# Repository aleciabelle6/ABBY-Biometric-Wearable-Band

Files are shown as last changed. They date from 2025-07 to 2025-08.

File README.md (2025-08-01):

# Anxiety Buddy Band for Youth (ABBY) - Biometric Wearable Band  
_Alecia Barbieri — Princeton University ECE Funded Summer Internship, 2023_

## Project Overview

This repository contains the KiCad design files for a custom Electrodermal Activity (EDA) and heart rate/blood oxygen sensor signal conditioning circuit. It integrates analog signal conditioning stages to filter, amplify, and prepare the weak physiological signals from wearable electrodes and sensors for digitization. This project involved extending and enhancing the Open-Smartwatch-Light open-source platform (https://open-smartwatch.github.io/) by advancing its electronic hardware and serves as my first exposure to KiCAD. 

The circuit is designed to amplify and clean signals from EDA electrodes, with additional capability for heart rate and blood oxygen sensing and position tracking. The design focuses on maximizing signal fidelity through multi-stage amplification and filtering, using a low-power LM324D operational amplifier.

---

## Circuit Extension Design Summary

Taking on this project with no prior experience in PCB design was a very daunting but nonetheless rewarding endeavor. As such, I gained so much knowledge from starting with an open-source PCB layout and extending the functionality of it. Below, I describe the various additions that I made to the design.

### Heart rate and Pulse Sensing

The BH1792GLC-E2 is an optical sensor that measures heart rate and pulse by detecting changes in blood volume using reflected green light. It emits green light through integrated LEDs and captures the reflected signal from skin tissue using a photodiode. This reflected light varies with blood flow, allowing the sensor to extract photoplethysmography (PPG) pulse wave information that is digitized internally and outputt via I2C to the ESP32 microcontroller. The sensor operates with precise timing control and built-in ambient light cancellation for the purpose of enhancing signal quality and reducing noise.

### EDA Sensor Signal Processing

EDA (Electrodermal Activity) electrodes measure changes in skin conductance caused by sweat gland activity, which reflects stress levels. I designed an analog signal conditioning chain that consists of three distinct stages, each implemented using one of the four internal amplifiers in the LM324D quad op-amp IC, for the purpose of having access to noise-free, clear, and useful data that can inform the microcontroller on parts of the physiological makeup that even the user isn't aren't aware of. The raw EDA signal interfaces with the board through an SJ-3524 connector. From there it gets processed through a 3-stage amplifier. The first stage is a differential amplifier stage, which takes in the raw EDA electrode signals, biased with a 1.65 V reference to accommodate single-supply operation and amplifies the differential signal from the electrodes while rejecting common-mode noise and interference. The second stage is an active low-pass filter stage which attenuates high-frequency noise and artifacts, preserving the low-frequency physiological signals typical in EDA and heart rate sensing. The third and final stage is the gain stage, which provides a gain of 11 to bring the signal into an optimal range for analog-to-digital conversion. This conditioned final signal then gets sent to an ADC input that then interfaces with the I2C protocols of the ESP32 at address 0x48.  

### Miscellaneous Changes
I changed the circular Open-Smartwatch-Light into a rectangular board to have enough room to accommodate the new devices. With this, I rerouted the entire board, prioritizing sectioning off analog, digital, and power lines as much as possible with the limited board space and also prioritized having sufficient trace width for the current passing through each branch of the circuit. 

---

## Circuit Component Overview

This section highlights the different components' functions in the circuit as visually depicted in the image below.

<p align="center">
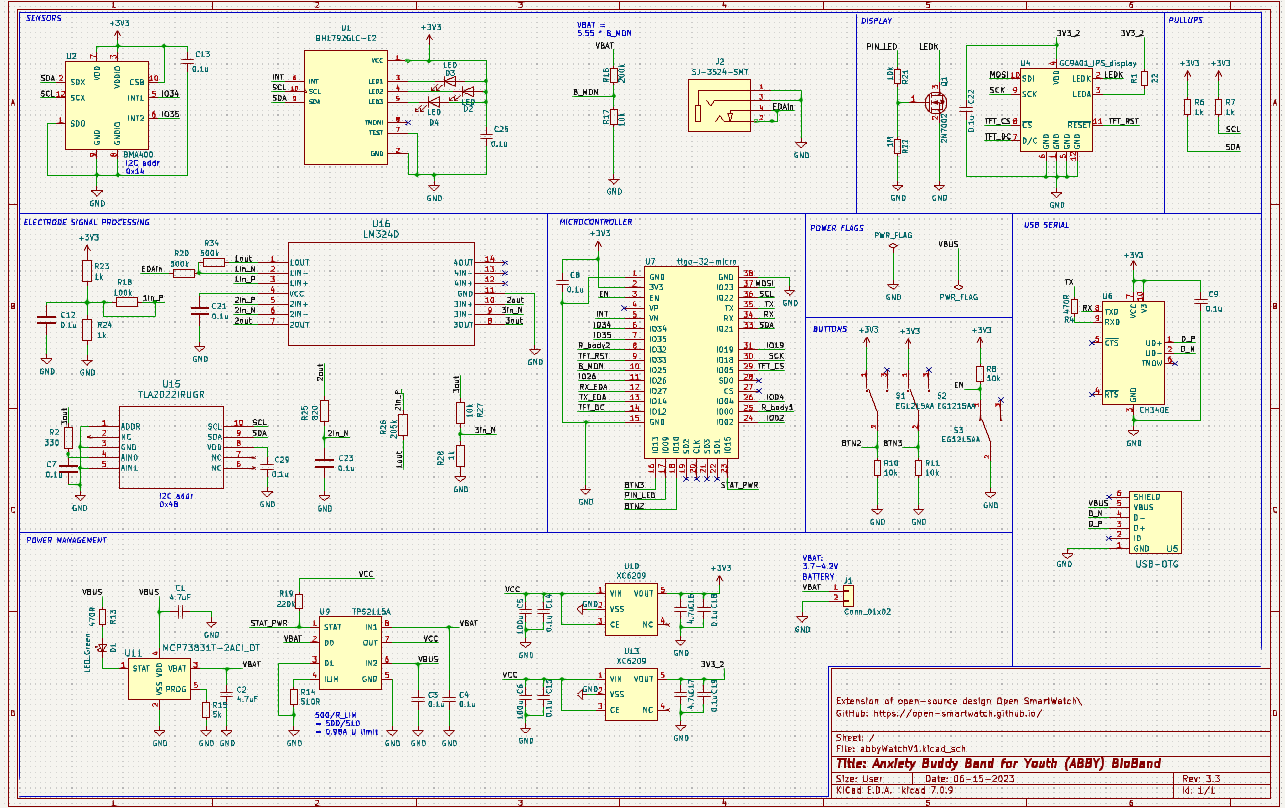
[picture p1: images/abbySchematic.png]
Circuit Schematic
  
</p>

The TTGO T-Micro32 V2.0 (ESP32-based Microcontroller) was used due to its very compact size, coming in at 45% smaller than standard ESP32. It has full GPIO support, Wi-Fi and Bluetooth features, and advanced power-saving features including clock gating, deep sleep, and dynamic power delegation. This microcontroller controls all of the devices, primarily using I2C to communicate with the different sensors as well as the ADC converter.

As far as sensing, the BH1792GLC-E2 ECG/PPG Heart Rate and Oximeter Sensor is an IR-based pulse wave sensor for heart rate and SpO2 monitoring. Communicates via I2C, uses interrupt-based burst reads, and includes bypass capacitors for power stability. The BMA400 3-axis accelerometer is an ultra-low power accelerometer for motion and activity tracking. It integrates with I2C, uses INT pin for data-ready alerts, and includes bypass capacitor for voltage filtering. The board supports an external pair of EDA electrodes spaced 4 cm apart at the top and bottom of the wrist for optimal skin conductance sensing. They are routed through SJ-3524 connector, then through 3-stage amplifier, then through ADC, then to I2C. In order for the EDA electrodes to be able to interface with the rest of the electronics, it must have a SJ-3524-SMT connector jack as seen in this pair of EDA electrodes: https://lafayettepolygraph.com/products/eda-assembly-7ft-lx6/. Throughout the board there are many capacitors used for voltage stability, filtering, and transient suppression across biosensors, power supply, and signal lines. Resistors are also employed in various places for pulling up the I2C lines as well as noise cancelling, as seen in the low pass filter for the EDA electrode signals.

The GC9A01 IPS Display: 1.28” circular IPS LCD with SPI interface, parallel RGB support, and adjustable brightness via 2N7002 transistor switch, which happenss by adjusting current through the LEDK pin on the GC9A01 screen, which in turn adjusts the backllight brightness of the display. This display screen offers wide viewing angles and vibrant display quality. There are also 3 SPST Buttons used for power enable (EN pin control) and general-purpose user inputs (e.g. calibrate, transmit).

The power delegation of the board is quite intuitive. The board is powered by a 3.7V LiPo battery with shorting protection; monitored via voltage divider and B_MON pin for on-screen battery status display. The MCP73831 LiPo Charging Management Controller is a constant-current/voltage charger with thermal regulation, charge termination, and USB-powered battery input for safe, efficient battery management. The TPS2115A Power Multiplexer is a smart autoswitching between USB and battery power sources based on availability and voltage conditions. It acts very similiar to a rely in that it relies on the battery level of the battery to determine which input to transfer to the output and to the next stage of the power management system. The PCB also contains 2 XC6209 LDO Voltage regulators that convert the output of the multiplexer to a consistent 3.3V output regardless of the input level, allowing for consistent operation of sensor powering and the main logic throughout the circuit. The micro-USB port has two functions as it takes in a charging cable to charge the onboard Li-Po battery using a regulated charging circuit, and this port also provides a data interface for uploading firmware to the microcontroller. This enables both power management and programming through a single, convenient connection. With this, the CH340E chip is a USB to Serial Converter converts the inputs of the micro-USB to UART to connect with the microcontroller to upload firmware. 

---

## PCB Circuit Layout Images

Below is the 3D circuit layout of the board followed by the front and back viewport as well as a 3D isometric viewport. As seen from the images below, the front of the board hosts the sensors, processors, buttons, external wire inputs, and passive components that sit on the side of the wrist in order to allow for the heart rate/pulse sensor to be able to better interface with the wrist. The back of the PCB contains the interfaces for the screen display and the external 3.7 LiPo battery, which is hosted below the screen but above the PCB.

<p align="center">
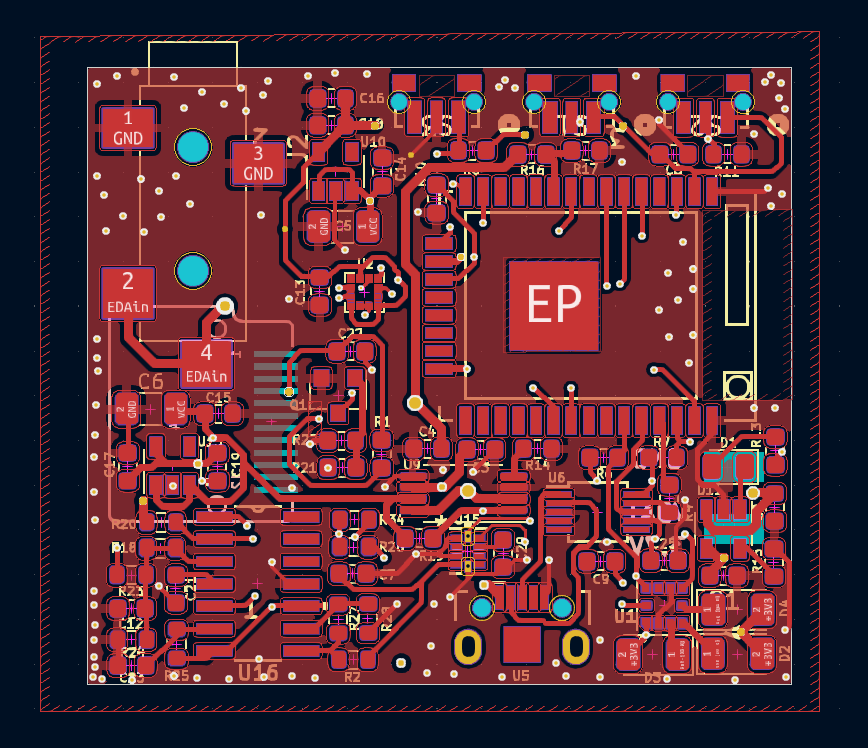
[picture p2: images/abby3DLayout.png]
  
</p>

<p align="center">
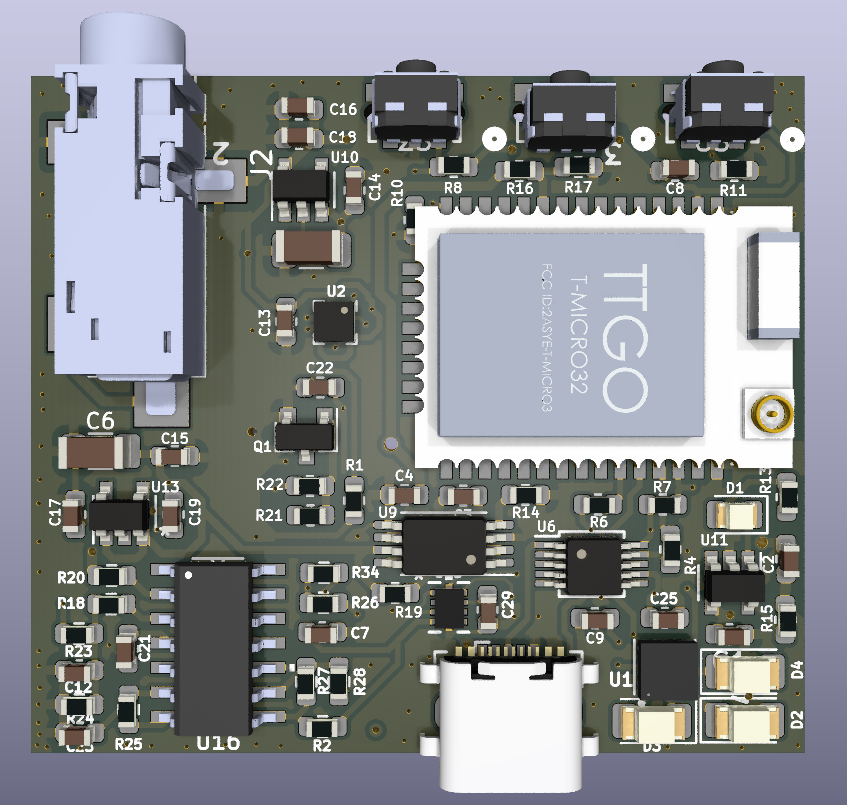
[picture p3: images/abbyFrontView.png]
PCB Front Viewport
  
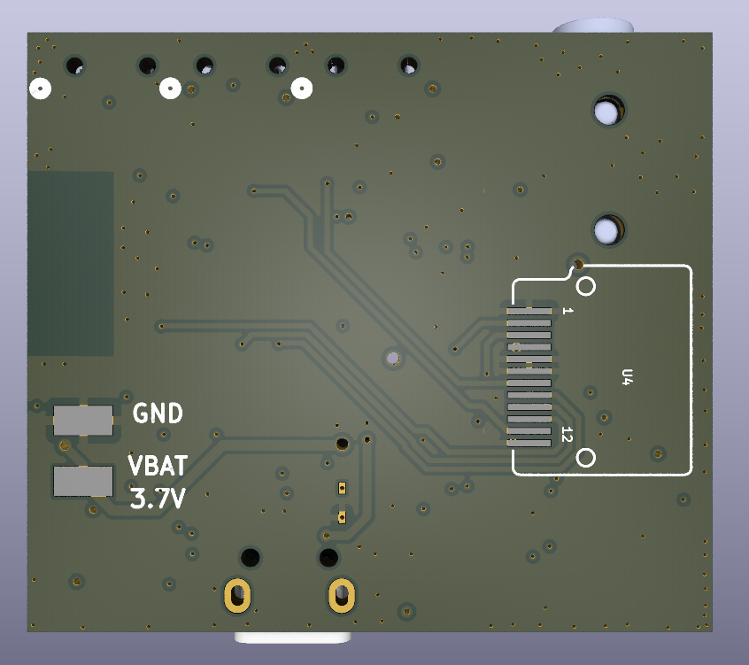
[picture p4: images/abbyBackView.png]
PCB Back Viewport
  
</p>

<p align="center">
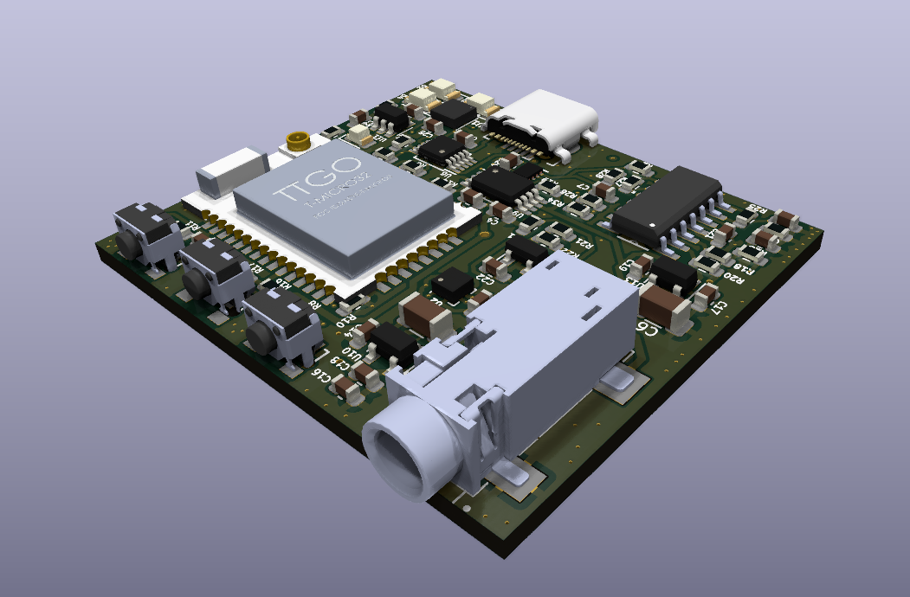
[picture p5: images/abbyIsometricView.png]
  
</p>

---

## Repository Contents

- **KiCad Project Files:** Schematic, PCB layout, and BOM files for the full EDA signal conditioning circuit.
- **EDA Models:** The symbol, footprint, and 3D CAD model for each component on the PCB.
- **Datasheets:** Relevant datasheets for each component.

## Getting Started

1. Clone the repository:
   ```bash
   git clone https://github.com/aleciabelle6/ABBY-Biometric-Wearable-Band.git
   cd ABBY-Biometric-Wearable-Band
2. On KiCAD, select **File > Open Project**.
3. Navigate to where you cloned this repository and open the file *abbyWatchV1.kicad_pro*. 

## License

This project is made available for academic, non-commercial use. Please contact me if you'd like to use any part of the content or code beyond that scope.

---
*Author: Alecia Barbieri ([LinkedIn](https://www.linkedin.com/in/aleciabarbieri))*  
*Project Advisor: Dr. David Wentzlaff*  
*Department of Electrical and Computer Engineering, Princeton University*

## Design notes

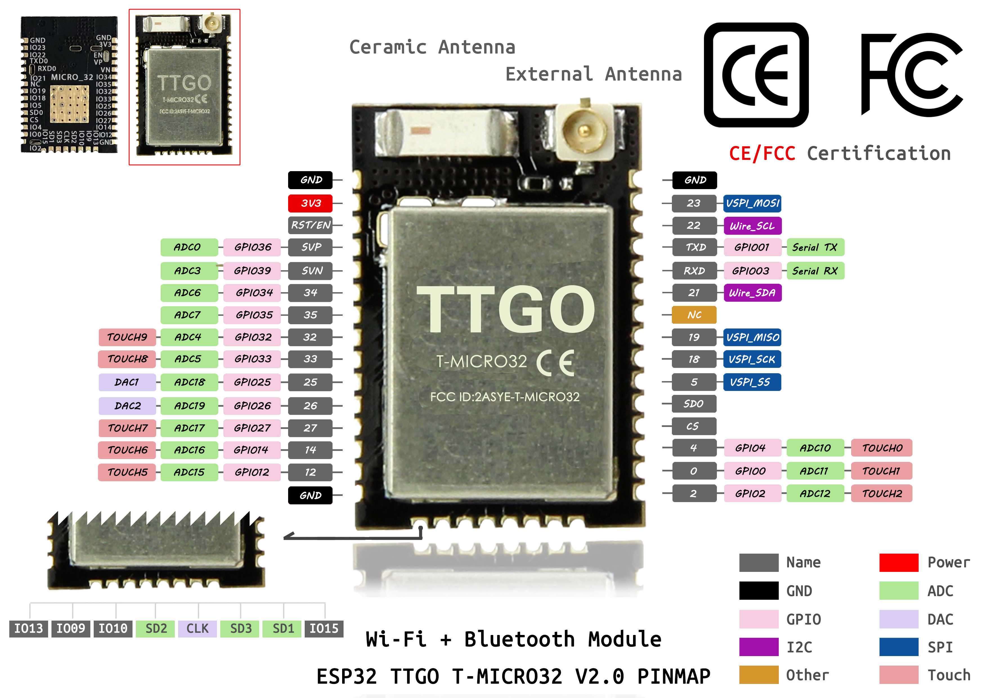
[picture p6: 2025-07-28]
docs/LILYGO-TTGO-Micro-32-V2-0.jpg

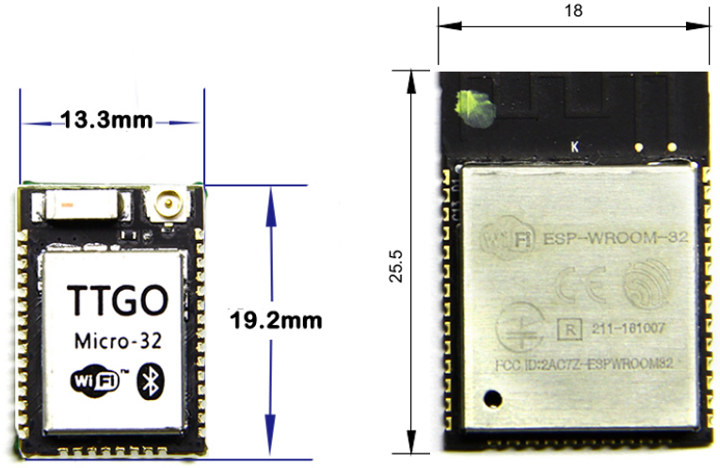
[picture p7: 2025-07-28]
docs/TTGO-Micro-32-vs-ESP32-WROOM-32.jpg

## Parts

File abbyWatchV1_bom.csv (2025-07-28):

Tool: | Eeschema 7.0.9
Generator: | C:\Users\aleci\OneDrive\bin\scripting\plugins/bom_csv_grouped_by_value.py
Component Count: | 69
Collated Components:
Item | Qty | Reference(s) | Value | LibPart | Footprint | Datasheet | MPN | Manufacturer
1 | 2 | C1, C2 | 4.7uF | Device:C_Small | Capacitor_SMD:C_0603_1608Metric | General | General | General
2 | 12 | C3, C4, C8, C9, C13, C14, C15, C18, C19, C22, C25, C29 | 0.1u | Device:C_Small | Capacitor_SMD:C_0603_1608Metric | General | General | General
3 | 2 | C5, C6 | 100u | Device:C_Small | Capacitor_SMD:C_1206_3216Metric | General | General | General
4 | 4 | C7, C12, C21, C23 | 0.1u | Device:C | Capacitor_SMD:C_0603_1608Metric | General | General | General
5 | 2 | C16, C17 | 4.7u | Device:C_Small | Capacitor_SMD:C_0603_1608Metric | General | General | General
6 | 1 | D1 | LED_Green | Device:LED_Small | LED_SMD:LED_0805_2012Metric | General | General | General
7 | 3 | D2, D3, D4 | LED | Device:LED | LED_SMD:LED_1206_3216Metric | General | General | General
8 | 1 | J1 | Conn_01x02 | Connector_Generic:Conn_01x02 | Connector_PinHeader_2.54mm:PinHeader_1x02_P2.54mm_Vertical | General | General | General
9 | 1 | J2 | SJ-3524-SMT | SJ3524:SJ-3524-SMT | SJ3524:CUI_SJ-3524-SMT | https://www.sameskydevices.com/product/resource/sj-352x-smt.pdf | SJ-352X-SMT | same sky
10 | 1 | Q1 | 2N7002 | Transistor_FET:2N7002 | Package_TO_SOT_SMD:SOT-23 | https://www.fairchildsemi.com/datasheets/2N/2N7002.pdf |  | onsemi
11 | 1 | R1 | 22 | Device:R_Small | Resistor_SMD:R_0603_1608Metric | General | General | General
12 | 1 | R2 | 330 | Device:R | Resistor_SMD:R_0603_1608Metric | General | General | General
13 | 2 | R4, R13 | 470R | Device:R_Small | Resistor_SMD:R_0603_1608Metric | General | General | General
14 | 2 | R6, R7 | 1k | Device:R_Small | Resistor_SMD:R_0603_1608Metric | General | General | General
15 | 5 | R8, R10, R11, R17, R21 | 10k | Device:R_Small | Resistor_SMD:R_0603_1608Metric | General | General | General
16 | 1 | R14 | 510R | Device:R_Small | Resistor_SMD:R_0603_1608Metric | General | General | General
17 | 1 | R15 | 5k | Device:R_Small | Resistor_SMD:R_0603_1608Metric | General | General | General
18 | 1 | R16 | 200k | Device:R_Small | Resistor_SMD:R_0603_1608Metric | General | General | General
19 | 1 | R18 | 100k | Device:R | Resistor_SMD:R_0603_1608Metric | General | General | General
20 | 1 | R19 | 220k | Device:R_Small | Resistor_SMD:R_0603_1608Metric | General | General | General
21 | 2 | R20, R34 | 500k | Device:R | Resistor_SMD:R_0603_1608Metric | General | General | General
22 | 1 | R22 | 1M | Device:R_Small | Resistor_SMD:R_0603_1608Metric | General | General | General
23 | 3 | R23, R24, R28 | 1k | Device:R | Resistor_SMD:R_0603_1608Metric | General | General | General
24 | 1 | R25 | 820 | Device:R | Resistor_SMD:R_0603_1608Metric | General | General | General
25 | 1 | R26 | 205k | Device:R | Resistor_SMD:R_0603_1608Metric | General | General | General
26 | 1 | R27 | 10k | Device:R | Resistor_SMD:R_0603_1608Metric | General | General | General
27 | 3 | S1, S2, S3 | EG1215AA | switches:EG1215AA | buttons:CONN3_3033816_WRE | https://configured-product-images.s3.amazonaws.com/Datasheets/EG1215.pdf | EG1215AA | E-Switch
28 | 1 | U1 | BH1792GLC-E2 | pulse:BH1792GLC-E2 | pulse:XDCR_BH1792GLC-E2 | https://fscdn.rohm.com/en/products/databook/datasheet/ic/sensor/pulse_wave/bh1792glc-e.pdf | BH1792GLC | Rohm Semiconductor
29 | 1 | U2 | BMA400 | open-Smartwatch:BMA400 | open-Smartwatch:narrow0.19mmV2BMA400 | https://ae-bst.resource.bosch.com/media/_tech/media/datasheets/BST-BMA400-DS000.pdf | BMA400 | Bosch Sensortec
30 | 1 | U4 | GC9A01_IPS_display | open-Smartwatch:GC9A01_IPS_display_SPI | open-Smartwatch:GC9A01_IPS_display | https://www.buydisplay.com/download/ic/GC9A01A.pdf | GC9A01A | GalaxyCore
31 | 1 | U5 | USB-OTG | open-Smartwatch:USB-OTG | open-Smartwatch:USBmicro-B | https://www.ti.com/lit/ml/sprp605/sprp605.pdf | General | General
32 | 1 | U6 | CH340E | open-Smartwatch:CH340E | open-Smartwatch:MSOP-10_3x3mm_P0.5mm | https://www.mpja.com/download/35227cpdata.pdf
33 | 1 | U7 | ttgo-32-micro | open-Smartwatch:ttgo-32-micro | open-Smartwatch:ttgo-32-micro | https://github.com/LilyGO/TTGO-Micro32-V2.0/blob/master/Datasheet/micro32%202020.3.4(1).pdf | TTGO Micro?32 V2.0 | LILYGO
34 | 1 | U9 | TPS2115A | open-Smartwatch:TPS2115A_default | open-Smartwatch:TSSOP-8_4.4x3mm_P0.65mm | https://www.ti.com/lit/ds/symlink/tps2114a.pdf?HQS=TI-null-null-digikeymode-df-pf-null-wwe&ts=1599026024238 | TPS2115APWR | Texas Instruments
35 | 2 | U10, U13 | XC6209 | open-Smartwatch:XC6209 | Package_TO_SOT_SMD:SOT-23-5 | https://product.torexsemi.com/system/files/series/xc6209.pdf | XC6209 | Torex Semiconductors Ltd.
36 | 1 | U11 | MCP73831T-2ACI_OT | open-Smartwatch:MCP73831T-2ACI_OT | open-Smartwatch:SOT-23-5 | https://www.digikey.com/en/products/detail/microchip-technology/MCP73831T-2ACI-OT/964301?gclsrc=aw.ds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 | MCP73831T-2ACI/OT | Microchip Technology
37 | 1 | U15 | TLA2022IRUGR | TLA2022:TLA2022IRUGR | TLA2022:RUG10_TEX | https://www.ti.com/lit/gpn/tla2022 | TLA2022IRUGR | Texas Instruments
38 | 1 | U16 | LM324D | LM324:LM324D | LM324D:D14 | https://www.ti.com/lit/gpn/lm324 | LM324D | Texas Instruments

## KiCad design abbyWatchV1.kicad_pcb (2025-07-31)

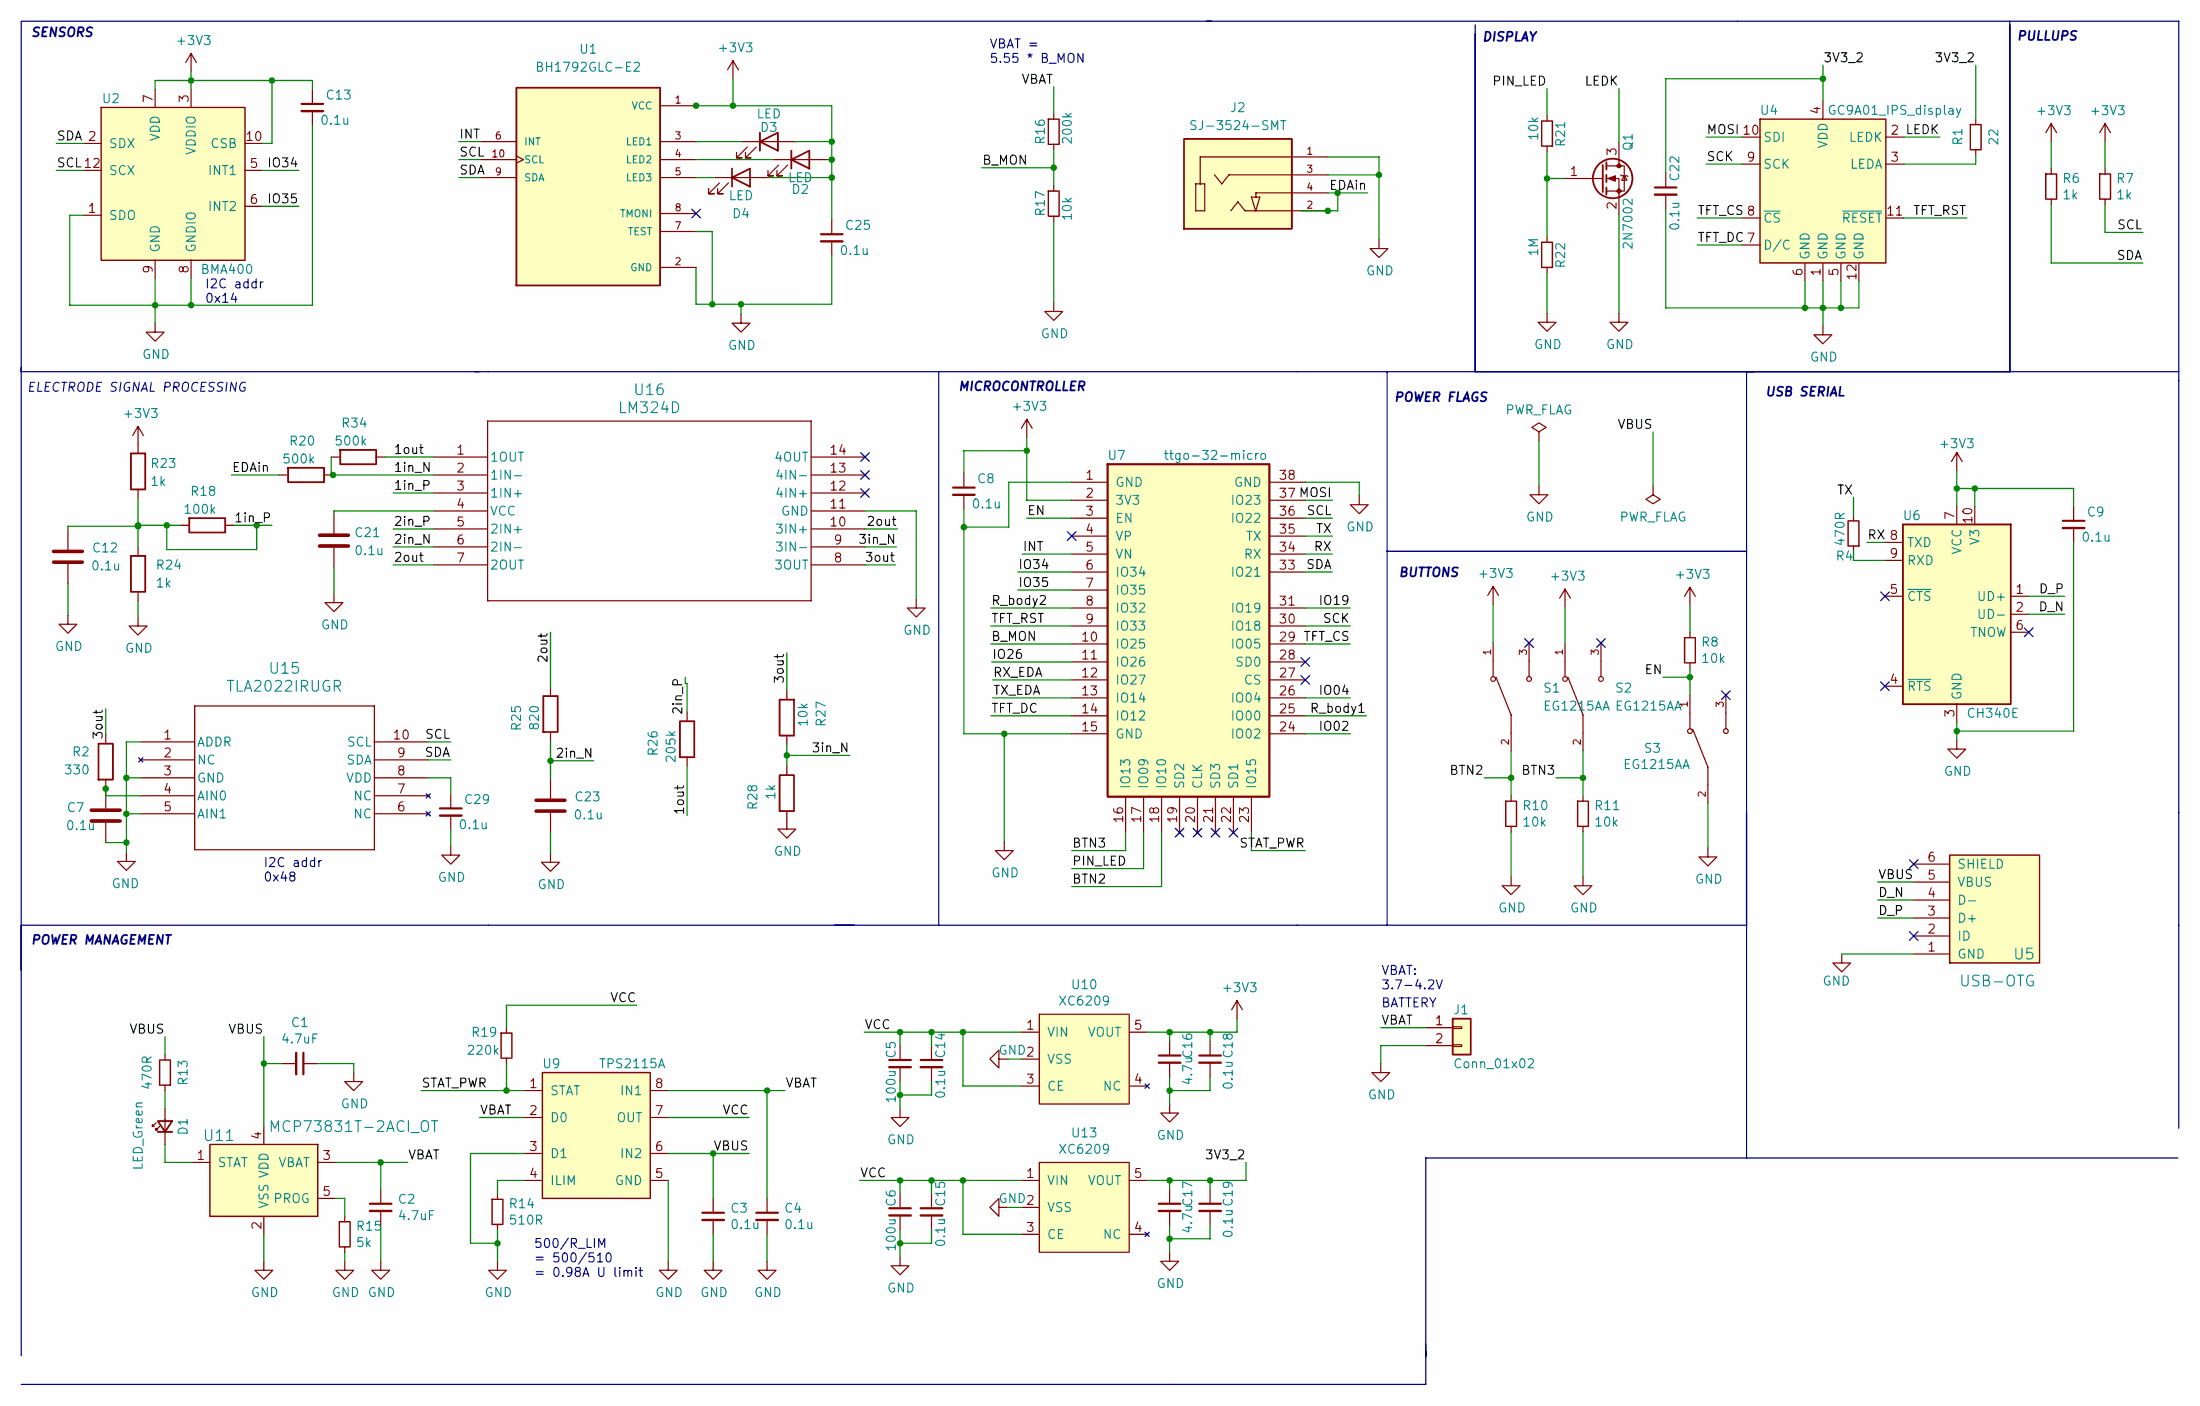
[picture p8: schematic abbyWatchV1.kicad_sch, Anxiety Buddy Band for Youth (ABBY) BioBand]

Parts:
C1, C2: 4.7uF; C_0603_1608Metric
C3, C4, C7, C8, C9, C12, C13, C14, C15, C18, C19, C21, C22, C23, C25, C29: 0.1u; C_0603_1608Metric
C5, C6: 100u; C_1206_3216Metric
C16, C17: 4.7u; C_0603_1608Metric
D1: LED_Green; LED_0805_2012Metric
D2, D3, D4: LED; LED_1206_3216Metric
J1: Conn_01x02; PinHeader_1x02_P2.54mm_Vertical
J2: SJ-3524-SMT; CUI_SJ-3524-SMT; PARTREV 1.03
Q1: 2N7002; SOT-23
R1: 22; R_0603_1608Metric
R2: 330; R_0603_1608Metric
R4, R13: 470R; R_0603_1608Metric
R6, R7, R23, R24, R28: 1k; R_0603_1608Metric
R8, R10, R11, R17, R21, R27: 10k; R_0603_1608Metric
R14: 510R; R_0603_1608Metric
R15: 5k; R_0603_1608Metric
R16: 200k; R_0603_1608Metric
R18: 100k; R_0603_1608Metric
R19: 220k; R_0603_1608Metric
R20, R34: 500k; R_0603_1608Metric
R22: 1M; R_0603_1608Metric
R25: 820; R_0603_1608Metric
R26: 205k; R_0603_1608Metric
S1, S2, S3: EG1215AA; CONN3_3033816_WRE; PARTREV A
U1: BH1792GLC-E2; XDCR_BH1792GLC-E2; PARTREV 002
U2: BMA400; narrow0.19mmV2BMA400; MPN BMA400; DigiKey_PN 828-1081-1-ND
U4: GC9A01_IPS_display
U5: USB-OTG; USBmicro-B
U6: CH340E; MSOP-10_3x3mm_P0.5mm
U7: ttgo-32-micro
U9: TPS2115A; TSSOP-8_4.4x3mm_P0.65mm; MPN TPS2115APWR; DigiKey_PN 296-16940-1-ND
U10, U13: XC6209; SOT-23-5
U11: MCP73831T-2ACI_OT; SOT-23-5; MPN MCP73831T-2ACI/OT; Digi-Key_PN MCP73831T-2ACI/OTCT-ND
U15: TLA2022IRUGR; RUG10_TEX
U16: LM324D; D14

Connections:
+3V3: C8.1, C9.1, C13.1, C16.1, C18.1, C25.1, D2.2 (A), D3.2 (A), D4.2 (A), R6.1, R7.1, R8.1, R23.2, S1.1, S2.1, U1.1 (VCC), U2.3 (VDDIO), U2.7 (VDD), U2.10 (CSB), U6.7 (VCC), U6.10 (V3), U7.2 (3V3), U10.5 (VOUT)
/1in_N: R20.1, R34.2, U16.2 (1IN-)
/1in_P: C12.1, R18.1, R18.2, R23.1, R24.2, U16.3 (1IN+)
/1out: R26.2, R34.1, U16.1 (1OUT)
/2in_N: C23.1, R25.2, U16.6 (2IN-)
/2in_P: R26.1, U16.5 (2IN+)
/2out: R25.1, U16.7 (2OUT), U16.10 (3IN+)
/3V3_2: C17.1, C19.1, C22.1, R1.1, U4.4 (VDD), U13.5 (VOUT)
/3in_N: R27.1, R28.1, U16.9 (3IN-)
/3out: R2.1, R27.2, U16.8 (3OUT)
/BTN2: R10.1, S1.2, U7.18 (IO10)
/BTN3: R11.1, S2.2, U7.16 (IO13)
/B_MON: R16.2, R17.1, U7.10 (IO25)
/D_N: U5.4 (D-), U6.2 (UD-)
/D_P: U5.3 (D+), U6.1 (UD+)
/EDAin: J2.2, J2.4, R20.2
/EN: R8.2, S3.1, U7.3 (EN)
/INT: U1.6 (INT), U7.5 (VN)
/IO02: U7.24 (IO02)
/IO04: U7.26 (IO04)
/IO19: U7.31 (IO19)
/IO26: U7.11 (IO26)
/IO34: U2.5 (INT1), U7.6 (IO34)
/IO35: U2.6 (INT2), U7.7 (IO35)
/LEDK: Q1.3 (D), U4.2 (LEDK)
/MOSI: U4.10 (SDI), U7.37 (IO23)
/PIN_LED: R21.2, U7.17 (IO09)
/RX: U6.8 (TXD), U7.34 (RX)
/RX_EDA: U7.12 (IO27)
/R_body1: U7.25 (IO00)
/R_body2: U7.8 (IO32)
/SCK: U4.9 (SCK), U7.30 (IO18)
/SCL: R7.2, U1.10 (SCL), U2.12 (SCX), U7.36 (IO22), U15.10 (SCL)
/SDA: R6.2, U1.9 (SDA), U2.2 (SDX), U7.33 (IO21), U15.9 (SDA)
/STAT_PWR: R19.2, U7.23 (IO15), U9.1 (STAT)
/TFT_CS: U4.8 (~CS), U7.29 (IO05)
/TFT_DC: U4.7 (D/C), U7.14 (IO12)
/TFT_RST: U4.11 (~RESET), U7.9 (IO33)
/TX: R4.2, U7.35 (TX)
/TX_EDA: U7.13 (IO14)
/VBAT: C2.1, C4.1, J1.1, R16.1, U9.2 (D0), U9.8 (IN1), U11.3 (VBAT)
/VBUS: C1.2, C3.1, R13.2, U5.5 (VBUS), U9.6 (IN2), U11.4 (VDD)
/VCC: C5.1, C6.1, C14.1, C15.1, R19.1, U9.7 (OUT), U10.1 (VIN), U10.3 (CE), U13.1 (VIN), U13.3 (CE)
GND: C1.1, C2.2, C3.2, C4.2, C5.2, C6.2, C7.2, C8.2, C9.2, C12.2, C13.2, C14.2, C15.2, C16.2, C17.2, C18.2, C19.2, C21.2, C22.2, C23.2, C25.2, C29.2, J1.2, J2.1, J2.3, Q1.2 (S), R10.2, R11.2, R14.2, R15.2, R17.2, R22.1, R24.1, R28.2, S3.2, U1.2 (GND), U1.7 (TEST), U2.1 (SDO), U2.8 (GNDIO), U2.9 (GND), U4.1 (GND), U4.5 (GND), U4.6 (GND), U4.12 (GND), U5.1 (GND), U6.3 (GND), U7.1 (GND), U7.15 (GND), U7.38 (GND), U9.3 (D1), U9.5 (GND), U10.2 (VSS), U11.2 (VSS), U13.2 (VSS), U15.1 (ADDR), U15.3 (GND), U15.5 (AIN1), U16.11 (GND)
unnamed: D1.2 (A), R13.1
unnamed: D1.1 (K), U11.1 (STAT)
unnamed: D2.1 (K), U1.4 (LED2)
unnamed: D3.1 (K), U1.3 (LED1)
unnamed: D4.1 (K), U1.5 (LED3)
unnamed: Q1.1 (G), R21.1, R22.2
unnamed: R1.2, U4.3 (LEDA)
unnamed: R4.1, U6.9 (RXD)
unnamed: R14.1, U9.4 (ILIM)
unnamed: R15.1, U11.5 (PROG)
unnamed: C7.1, R2.2, U15.4 (AIN0)
unnamed: C29.1, U15.8 (VDD)
unnamed: C21.1, U16.4 (VCC)

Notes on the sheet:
500/R_LIM = 500/510 = 0.98A U limit
VBAT = 5.55 * B_MON
I2C addr 0x14
SENSORS
POWER FLAGS
PULLUPS
ELECTRODE SIGNAL PROCESSING
BATTERY
USB SERIAL
BUTTONS
VBAT: 3.7-4.2V
MICROCONTROLLER
POWER MANAGEMENT
I2C addr 0x48
DISPLAY

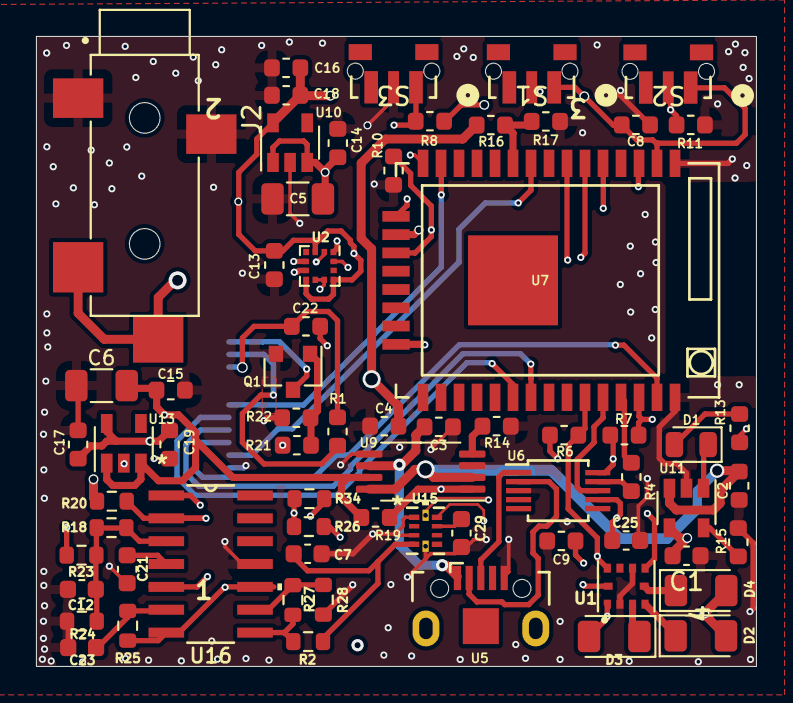
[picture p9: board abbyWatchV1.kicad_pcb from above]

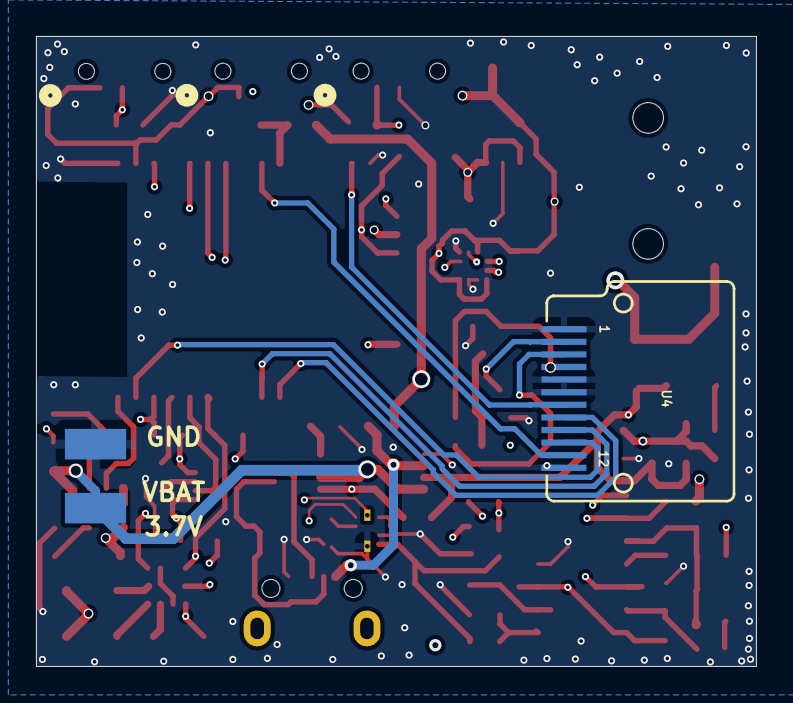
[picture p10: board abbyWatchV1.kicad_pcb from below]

Board: 4 copper layers, 40.0 x 35.0 mm, 69 parts (2 on the bottom side), 49 nets.

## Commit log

2025-07-28 Initial Commit: uploading all files
    [abbyWatchV1.kicad_pcb, abbyWatchV1.kicad_sch, abbyWatchV1_bom.csv, bb8DomeNeopixels-B_Adhesive.gbr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]
2025-07-31 Added project images and all component CAD models
    [abbyWatchV1.kicad_pcb]
2025-08-01 Update README.md
    Added project images, including visuals of the circuit schematic, 3D board layout, and front, back, and isometric viewports.
